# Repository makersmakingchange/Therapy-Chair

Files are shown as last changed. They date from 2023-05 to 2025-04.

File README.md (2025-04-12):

# Therapy Chair
ATP's, PT's, and OT's working with children with physical disabilities often need an appropriate seating system to provide support to enable the kiddo to engage with their environment and participate in strengthening exercises. In the past we measured each child and built it, usually out of triwall, to their size to ensure a good fit. The benefit of this new design is the chair is more durable/easier to clean than triwall and is adjustable. It resembles Swiss cheese to allow placement of laterals virtually anywhere. It can work as a chair or floor sitter. It can incline forward 5 degrees or lay all the way back flat. At the time we are writing this, the cost came in around $100/chair for 7 chairs that we made. This isn't going to work for every kiddo, but we leave it up to you to adapt it further for your unique situation.

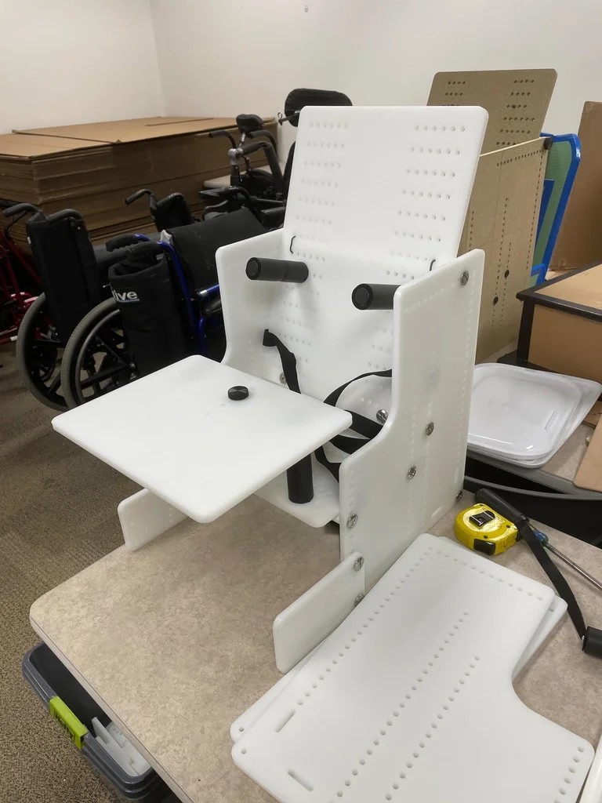
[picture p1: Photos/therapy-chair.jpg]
Picture of Therapy Chair.


<!--
## More info at
- [Makers Making Change Project Page](https://makersmakingchange.com/project/therapy-chair/)
-->

## How to Obtain a Therapy Chair
### 1. Do it Yourself (DIY) or Do it Together (DIT)

This is an open-source assistive technology, so anyone is free to build it. All of the files and instructions required to build the Therapy Chair are contained within this repository. Refer to the Maker Checklist below.

<!--
### 2. Request a build of this device

If you would like to obtain a Therapy Chair, you may submit a build request through the [MMC Library Page](https://makersmakingchange.com/project/therapy-chair/). The requestor is responsible for the cost of materials and any shipping.

### 3. How to build this device for someone else

If you have the skills and equipment to build this device, and would like to donate your time to create the switch for someone who needs it, visit the [MMC Maker Wanted](https://makersmakingchange.com/maker-wanted/) section.
-->

## Getting Started

### 1. Read the Makers Checklist

[The Makers Checklist](/Documentation/Therapy_Chair_Maker_Checklist_V1.0.pdf)

### 2. Order the Off-The-Shelf Components

The [Bill of Materials](/Documentation/Therapy_Chair_BOM_V1.0.xlsx) lists all of the parts and components required to build the Therapy Chair. The main switch component needs to be ordered online. The rest of the off-the-shelf components are also online or may be available in smaller quantities at your local hardware store or dollar store.

### 3. CNC Rout the body panels

The DXF files can be in the [CNC Files](/Build_Files/CNC_Files) folder.

### 4. Assemble the Therapy Chair

Reference the [Assembly Guide](/Documentation/Device-Name_Assembly_Guide_V1.0.pdf) for the tools and steps required to build each portion.

## Files
### Documentation
| Document             | Version | Link |
|----------------------|---------|------|
| Design Rationale     | 1.0     | [Therapy_Chair_Design_Rationale](/Documentation/Therapy_Chair_Design_Rationale_V1.0.pdf)     |
| Maker Checklist      | 1.0     | [Therapy_Chair_Maker_Checklist](/Documentation/Therapy_Chair_Maker_Checklist_V1.0.pdf)     |
| Bill of Materials    | 1.0     | [Therapy_Chair_Bill_of_Materials](/Documentation/Therapy_Chair_BOM_V1.0.xlsx)     |
| Assembly Guide       | 1.0     | [Therapy_Chair_Assembly_Guide](/Documentation/Therapy_Chair_Assembly_Guide_V1.0.pdf)     |
| User Guide           | 1.0     | [Therapy_Chair_User_Guide](/Documentation/Therapy_Chair_User_Guide_V1.0.pdf)    |
| Changelog            | 1.0     | [Therapy_Chair_Changelog](/Documentation/Therapy_Chair_Changelog_V1.0.pdf)     |

### Build Files
 - [CNC Files](/Build_Files/CNC_Files)

## Attribution
Designers:
 - [Design](https://www.instructables.com/Child-Therapy-Chair/) by [Utah Assistive Technology Program](https://www.instructables.com/member/uatpat/)
 - Documentation by Neil Squire Society/Makers Making Change

## License
Everything needed or used to design, make, test, or prepare the Therapy Chair is licensed under the [Attribution-NonCommercial-ShareAlike 4.0 ](https://creativecommons.org/licenses/by-nc-sa/4.0/).

Accompanying material such as instruction manuals, videos, and other copyrightable works that are useful but not necessary to design, make, test, or prepare the THerapy Chair are published under a Creative Commons Attribution-ShareAlike 4.0 license https://creativecommons.org/licenses/by-sa/4.0/ (CC BY-SA 4.0).

----

<!-- ABOUT MMC START -->
## About Makers Making Change
[Makers Making Change Logo](https://www.makersmakingchange.com/)

Makers Making Change is a program of [Neil Squire](https://www.neilsquire.ca/), a Canadian non-profit that uses technology, knowledge, and passion to empower people with disabilities.

Makers Making Change leverages the capacity of community based Makers, Disability Professionals and Volunteers to develop and deliver affordable Open Source Assistive Technologies.

 - Website: [www.MakersMakingChange.com](https://www.makersmakingchange.com/)
 - GitHub: [makersmakingchange](https://github.com/makersmakingchange)
 - Bluesky: [@makersmakingchange.bsky.social](https://bsky.app/profile/makersmakingchange.bsky.social)
 - Instagram: [@makersmakingchange](https://www.instagram.com/makersmakingchange)
 - Facebook: [makersmakechange](https://www.facebook.com/makersmakechange)
 - LinkedIn: [Neil Squire Society](https://www.linkedin.com/company/neil-squire-society/)
 - Thingiverse: [makersmakingchange](https://www.thingiverse.com/makersmakingchange/about)
 - Printables: [MakersMakingChange](https://www.printables.com/@MakersMakingChange)

### Contact Us
For technical questions, to get involved, or to share your experience we encourage you to [visit our website](https://www.makersmakingchange.com/) or [contact us](https://www.makersmakingchange.com/s/contact).
<!-- ABOUT MMC END -->

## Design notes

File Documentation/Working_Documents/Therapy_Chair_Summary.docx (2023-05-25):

# Title

Therapy Chair

## Subtitle

An adjustable therapy chair that is durable and easy to clean.

## Device Details

### Overview

ATP's, PT's, and OT's working with children with physical disabilities often need an appropriate seating system to provide support to enable the kiddo to engage with their environment and participate in strengthening exercises. In the past we measured each child and built it, usually out of triwall, to their size to ensure a good fit. The benefit of this new design is the chair is more durable/easier to clean than triwall and is adjustable. It resembles Swiss cheese to allow placement of laterals virtually anywhere. It can work as a chair or floor sitter. It can incline forward 5 degrees or lay all the way back flat. At the time we are writing this, the cost came in around $100/chair for 7 chairs that we made. This isn't going to work for every kiddo, but we leave it up to you to adapt it further for your unique situation.

### Usage

The overall height from floor to seat bottom can be adjusted by moving the seat bottom and seat back up and down.

The seat depth can be adjusted by repositioning where the hinge pipe bolts onto the seat base.

The seat back angle can be adjusted by moving the support pipe near the top of the seat back forward or back.

The seat base angle can be adjusted by moving the pipe near the front up or down.

Any of the laterals can be repositioned by unscrewing and bolting in a new hole.

The anti-tipper/foot mount has an arc of holes in it. If the child is put into a reclined position and their feet need something to sit on, you can raise and rotate the anti-tipper/foot mount to the appropriate position. From there, you will need to add on your own support, whether you use more sheet plastic or more pieces of PVC pipe to go between the foot mounts.

If the child needs a 5-point harness instead of a chest belt and lap belt, we have one listed on the parts list that was inexpensive. Wrap the straps around the seat back and secure the straps to whatever is appropriate (lateral bolt, PVC pipe, etc.)

### Cost

~$100 per chair

### Build Instructions

This build is mostly using hand tools, but with a small amount of CNC router use to make the body panels.

#### Skills Required

- CNC Routing
- Mechanical Assembly

#### Time Required

Assembly time: 1h

#### Tools

- CNC Router
- Hammer
- Screwdriver
- Scissors
- Tape Measure
- Saw

### Attribution

- Design (https://www.instructables.com/Child-Therapy-Chair/) by the Utah Assistive Technology Program (https://www.instructables.com/member/uatpat/)
- Documentation by Neil Squire Society/Makers Making Change

© 2023 by Neil Squire. This work is licensed under the CC BY SA 4.0 License: http://creativecommons.org/licenses/by-sa/4.0 Files available at https://makersmakingchange.com/project/therapy-chair/ Page 1 of 1

V1.0 | March 2023 Therapy Chair Summary

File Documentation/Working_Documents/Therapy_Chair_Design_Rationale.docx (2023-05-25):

# Introduction

ATP's, PT's, and OT's working with children with physical disabilities often need an appropriate seating system to provide support to enable the kiddo to engage with their environment and participate in strengthening exercises. In the past each child was measured, and a chair built, usually out of Tri-Wall, to their size to ensure a good fit. A customizable therapy chair that can be adjusted in minutes, rather than built in days, would be a helpful tool to have.

# Research

After research, it was found that therapy chairs are commonly custom built to the measurements of each child. This requires the therapist to take measurements and design a custom chair for each new patient. There is a distinct lack of any ready made, adjustable chairs that can accommodate patients of various sizes.

# Requirements

## Goals

G01 | Create an adjustable therapy chair that is durable and easy to clean.

## Functional Requirements

F01 | Chair must be easy to adjust to the child
F02 | Chair must be durable
F03 | Chair must be able to hold the child securely

## Non-functional Requirement

NF01 | Chair must be easy to build
NF02 | Chair must be easy to clean
NF03 | Chair must not have sharp edges or be able to injure the child

## Constraints

C01 | Chair must be made of commonly available parts

# Opportunities for Improvement

Side panels could be updated so that they can be manufactured without the use of a CNC router

© 2023 by Neil Squire. This work is licensed under the CC BY SA 4.0 License: http://creativecommons.org/licenses/by-sa/4.0 Files available at https://makersmakingchange.com/project/therapy-chair/ Page 1 of 1

V1.0 | March 2023 Therapy Chair Design Rationale

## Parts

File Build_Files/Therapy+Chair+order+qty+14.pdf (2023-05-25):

Description | Order qty Total Cost
Charlotte Pipe 1/2‐in dia‐Degree 600 Psi Schedule 40 White PVC Pipe | 14 | 78.54 $ | https://www.lowes.com/pd/Charlotte‐Pipe‐1
S67‐244 3/4in Round | 1/4‐20 Thread Heavy Duty Double Star Metal Tube
Connector $0.48 ea. + $24.00 frieght (Pipe‐12, Laterals 6, Abductor 2) | 280 | 134.40 $

https://www.outwater.com/products/34in‐ro

Frieght S67‐244 3/4in Round | 1/4‐20 Thread | $ | 33.60
Hillman 831490 Stainless Steel Hurricane Bolts (1/4" x 1") ‐ 100 pieces (Pipe‐
16, Laterals 6, Abductor 1) | 3 | 84.57 $ | https://smile.amazon.com/dp/B00MEWLNAS
40Pcs Anwenk 1/4"‐20 x 20mm Furniture Screw in Nut Threaded Wood
Inserts Bolt Fastener Connector Hex Socket Drive for Wood Furniture
Assortment (with Hex Spanner) | 2 | 19.98 $

https://smile.amazon.com/Anwenk‐Furniture

Twenty (20) 1/4‐20 x 1" Long Length Knurled Plastic Head Thumb Screws ‐
Made in USA | 1 | 13.99 $ | https://smile.amazon.com/Twenty‐Length‐Kn
uxcell Foam Tubing for Handle Grip Support, Pipe Insulation, 20mm ID 30mm
OD 1m Length Black 39.37" (39/4"= 9.75) 7 ‐ 4" pieces | 12 | 155.88 $ | https://smile.amazon.com/uxcell‐Tubing‐Han

3/4 Inch Round Plastic Plug / 100 Pack / Black Tubing End Cap Plug / Used
with 14‐20 Gauge Tube Wall Thickness/Durable Chair Glide / Provides
Protection on Flooring (100) by EZENDS. | 1 | 29.81 $

https://smile.amazon.com/Plastic‐Thickness‐P

5 Point Harness Seat Belt Safety Harness Full Protection 5 Point Security
Harness Seatbelt for High Chair and Pushchair Black | 4 | 34.36 $ | https://smile.amazon.com/Harness‐Protectio
Saisn Reusable Fastening Tape Cable Ties 3/4 Inch Double Side Hook Roll (5
Yard, Black)5x3=15, 5.99/15=$0.40 ea. Set | 1 | 5.99 $ | https://smile.amazon.com/dp/B06Y2S7GKT/r

PQPB Garden Twist Ties Soft Reusable Rubber Wire Green Heavy Duty Plant
Support Twine for Gardening,Office,Home (2PCS X 32.8feet, Total
65.8feet),Green ,Rubber Plant Ties Green 65.6ft(PQ10) | 1 | 11.89 $ | https://smile.amazon.com/PQPB‐Reusable‐Ga
3/8 x 4 x 10 White HDPE Panel 80lbs/6 units=16lbs | 2 | 556.00 $
Labor to CNC | 2 | 200.00 $
Total Cost | | $ 1,359.01
Cost Each Chair | $ | 97.07

‐2‐in‐dia‐x‐10‐ft‐L‐600‐PSI‐PVC‐Pipe/3133079

ound‐14‐20‐thread‐heat‐treated‐carbon‐steel‐heavy‐duty‐double‐star‐metal‐tube‐connector/

/ref=twister_B082XW6FR6?_encoding=UTF8&psc=1

e‐Threaded‐Connector‐Assortment/dp/B07VLLKX32/ref=pd_bxgy_img_1/147‐7973450‐5835460?pd_rd_w=FJck7&pf_rd_p=6b3eefea‐7b16‐43e9‐bc45

nurled‐Plastic‐Screws/dp/B01N01IP6M/ref=sr_1_7?keywords=1%2F4‐20+x+1%22+Length+Knurled+Plastic+Head+Thumb+Screws&qid=1647979212&

dle‐Support‐Insulation/dp/B09521L1W2/ref=sr_1_2?crid=1XRFDUEZB6XI2&keywords=20mm%2Bfoam%2Btubing%2Bfor%2Bhandle%2Bgrip%2Bsupp

Provides‐Protection‐Flooring/dp/B07WDRKKZQ/ref=sr_1_9?crid=K1SKVJKQ03T0&keywords=round%2Bplastic%2Bplug%2B20mm%2F0.78&qid=16499

n‐Security‐Seatbelt‐Pushchair/dp/B08ZSHKCK6/ref=pb_allspark_dp_sims_pao_desktop_session_based_2/147‐7973450‐5835460?pd_rd_w=JR3A5&p

ref=twister_B06ZZ59XPX?_encoding=UTF8&psc=1

ardening‐32‐8feet‐65‐8feet/dp/B09H3Y5WB8/ref=sr_1_2_sspa?keywords=Rubber+Twist+Ties&qid=1648191290&sr=8‐2‐spons&psc=1&spLa=ZW5jcn

5‐2e332cbf99da&pf_rd_r=SWXYF3PATKNXXEZH9SE8&pd_rd_r=2325c0df‐c91a‐446d‐a659‐9110172d9653&pd_rd_wg=WTmdd&pd_rd_i=B07HR63VF

s=hi&sr=1‐7

port&qid=1646425796&s=hi&sprefix=20%2Bmm%2Bfoam%2Btubing%2Bfor%2Bhandle%2Bgrip%2Bsupport%2Ctools%2C153&sr=1‐2&th=1

968032&sprefix=round%2Bplastic%2Bplug%2B20%2Bmm%2F0.78%2Caps%2C103&sr=8‐9&th=1

pf_rd_p=e896123b‐6614‐49c5‐873e‐d532e726c2f0&pf_rd_r=R1QVC1M5B8A140S18FSR&pd_rd_r=7d37e6eb‐9433‐4b06‐b6bb‐f519dcca4df7&pd_rd_

nlwdGVkUXVhbGlmaWVyPUEyNEdURDNPRkY4QjU3JmVuY3J5cHRlZElkPUEwNTAzMzkzM0hWV1o2QlVHMlpGTSZlbmNyeXB0ZWRBZElkPUEwMjc4MzY

F5&th=1

_wg=nrkUs&pd_rd_i=B08ZSHKCK6&psc=1

YzMkZPOUlKMlMyR0pJNiZ3aWRnZXROYW1lPXNwX2F0ZiZhY3Rpb249Y2xpY2tSZWRpcmVjdCZkb05vdExvZ0NsaWNrPXRydWU=

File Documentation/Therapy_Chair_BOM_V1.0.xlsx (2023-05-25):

Device: Therapy Chair |  | Total Cost | Total Print time (hr) | Total filament (g)
Version: V1.0 | Date Created: 3/13/2023 | $169.64 | 0.00 | 0
Commercial Parts:
Part type (Electrical. Mechanical, Sanitization, ect) | Part Name | Quantity Needed | Pkg Quantity | Price per package | Price per Unit | Price for qty needed |  | Link
Mechanical | 1/2‐in dia‐Degree 600 Psi Schedule 40 White PVC Pipe | 8 | 10 | $4.71 | $0.47 | $3.77 |  | https://www.homedepot.com/p/JM-EAGLE-1-2-in-x-10-ft-600-PSI-White-Schedule-40-PVC-Pressure-Plain-End-Pipe-530048/100113200
Mechanical | Heavy Duty Double Star Metal Tube Connector | 20 | 1 | $1.25 | $1.25 | $25.00 |  | https://www.outwater.com/S67-PARENT?quantity=1&purchase-option=11&tube-size=1
Mechanical | Sidewalk Bolt 1/4 x 1 | 20 | 100 | $32.99 | $0.33 | $6.60 |  | Hillman Group Combo Sidewalk Bolt, Hurricane Hardware, 100 Pieces, Rust-Resistant, Durable, Truss Head, (1/4" x 1") Stainless Steel Finish (831490) (amazon.com) (https://www.amazon.com/dp/B00MEWLNAS?redirectFromSmile=1)
Mechanical | Anwenk 1/4"-20 x 20mm Furniture Screw | 1 | 40 | 18.45 | $0.46 | $0.46 |  | https://www.amazon.ca/Anwenk-Furniture-Threaded-Connector-Assortment/dp/B07VLLKX32?th=1
Mechanical | 1/4-20 x 1-1/2" Long Length Knurled Plastic Head Thumb Screws | 1 | 20 | 26.63 | $1.33 | $1.33 |  | https://www.amazon.ca/Twenty-Length-Knurled-Plastic-Screws/dp/B075VJKBLS
Mechanical | Foam Tubing for Handle Grip Support | 0.5 | 1 | 16.92 | $16.92 | $8.46 |  | Foam Grip Tubing Handle Grips Pipe Insulation,20mm ID 30mm OD 1m Length,Non-Slip for Fitness,Tools Handle Support,Black : Amazon.ca: Tools & Home Improvement (https://www.amazon.ca/Tubing-Insulation-Non-Slip-Fitness-Support/dp/B0BB278FRJ?s=hi)
Mechanical | Black Tubing End Cap Plug | 4 | 20 | 12.98 | $0.65 | $2.60 |  | https://www.amazon.ca/Round-Plastic-Tubing-Furniture-Insert/dp/B098QRJTBH
Mechanical | 5 Point Harness Seat Belt | 1 | 1 | 9.99 | $9.99 | $9.99 |  | https://www.amazon.com/Harness-Protection-Security-Seatbelt-Pushchair/dp/B08ZSHKCK6
Mechanical | Saisn Reusable Fastening Tape | 0.1 | 1 | 6.99 | $6.99 | $0.70 |  | Saisn Reusable Fastening Tape Cable Ties 3/4 Inch Double Side Hook Roll (5 Yard, Black) (amazon.com) (https://www.amazon.com/dp/B06Y2S7GKT/r?redirectFromSmile=1)
Mechanical | Heavy Duty Plant Support Twine | 0.05 | 1 | 11.98 | $11.98 | $0.60 |  | https://www.amazon.com/PQPB-Reusable-Gardening-32-8feet-65-8feet/dp/B09H3Y5WB8
Mechanical | 3/8" x 48" x 96" HDPE Sheet | 0.4 | 1 | 275.35 | $275.35 | $110.14 | Plywood can be used here | https://www.usplastic.com/catalog/item.aspx?itemid=41935
3D Printed Parts ESTIMATED PRICING USING 1KG ROLL COST: | $25.00
Part | Description | Quantity Needed | TOTAL Mass (g) | Estimated Price | Print Time (Min) | Link
See build files for CNC DXF files |  |  |  | $0.00
 |  |  |  | $0.00
 |  |  |  | $0.00
 |  |  |  | $0.00
 |  |  |  | $0.00
 |  |  | Total Print Cost: | $0.00
Tools for Assembly
Alternatives (if there are other sources for some parts link them below)
Part and description | Link
PVC pipe | https://www.amazon.ca/Pipe-Sch40-White-Custom-Length/dp/B09GL4G2MC

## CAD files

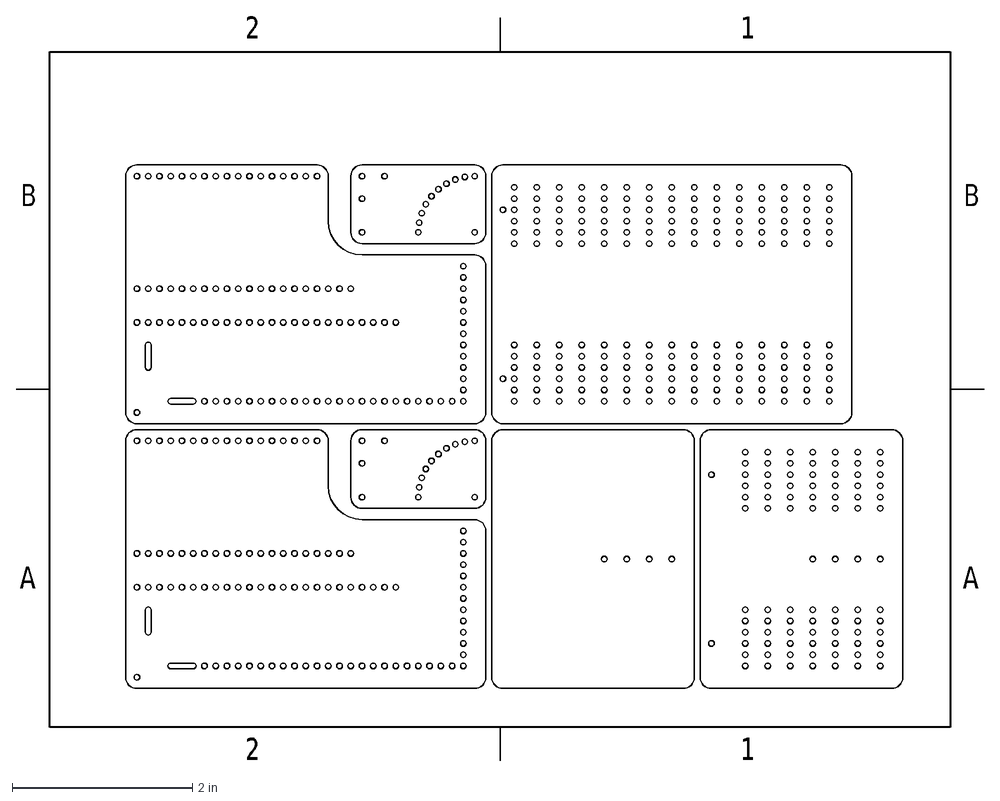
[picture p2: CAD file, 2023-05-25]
Build_Files/CNC_Files/sheet+parts+layout.DXF
A
B
2
1

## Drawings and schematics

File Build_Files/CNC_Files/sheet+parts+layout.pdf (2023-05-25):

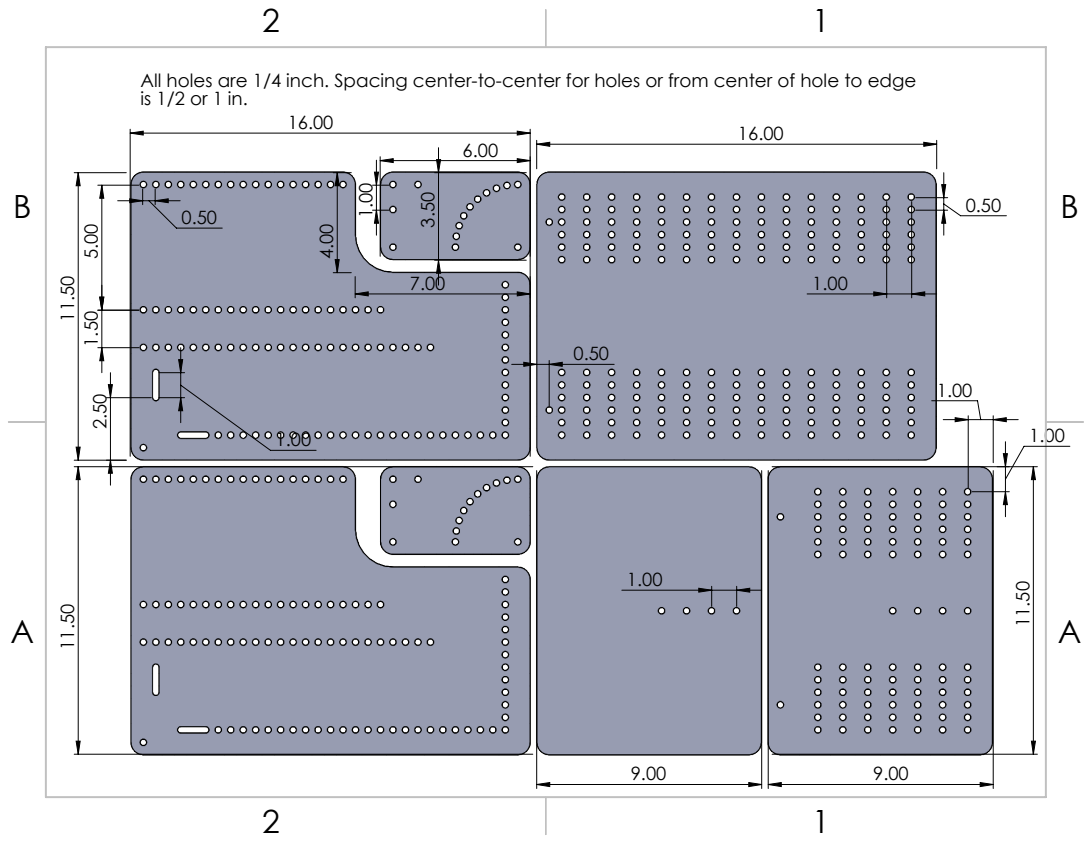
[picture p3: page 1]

All holes are 1/4 inch. Spacing center-to-center for holes or from center of hole to edge

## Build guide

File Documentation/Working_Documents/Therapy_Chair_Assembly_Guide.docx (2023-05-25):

# Required Components

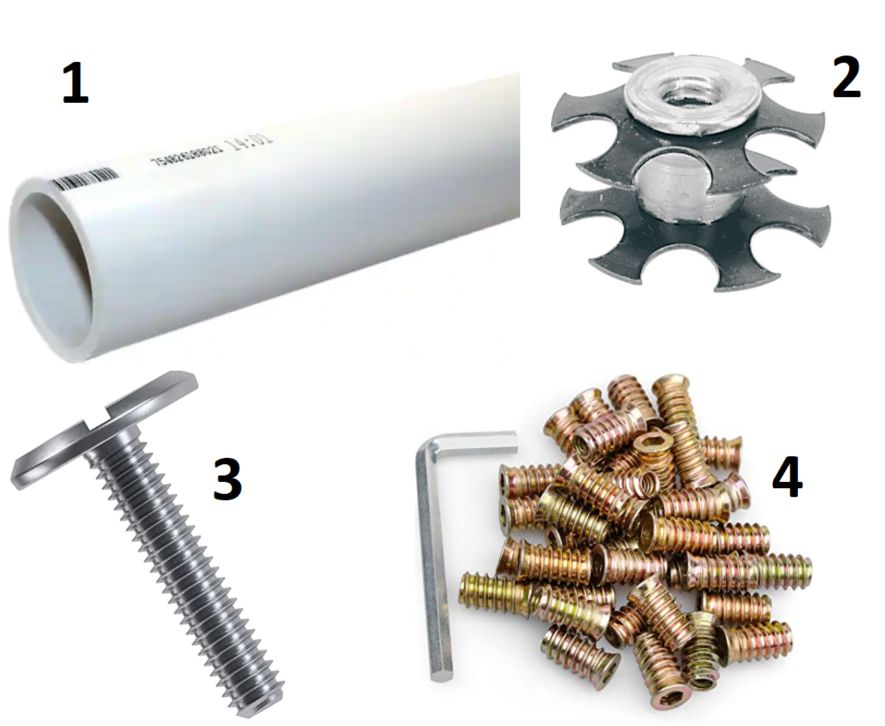
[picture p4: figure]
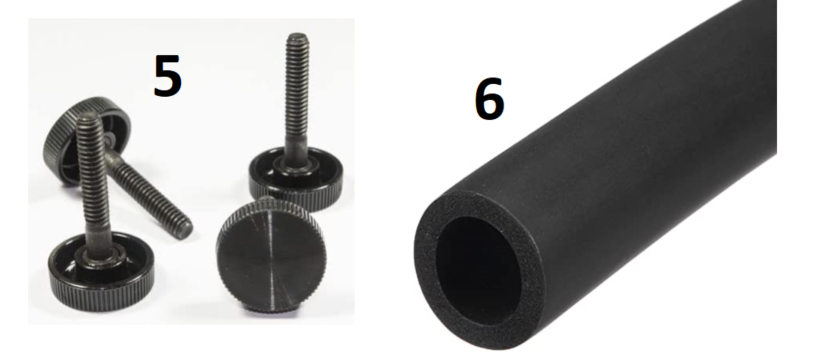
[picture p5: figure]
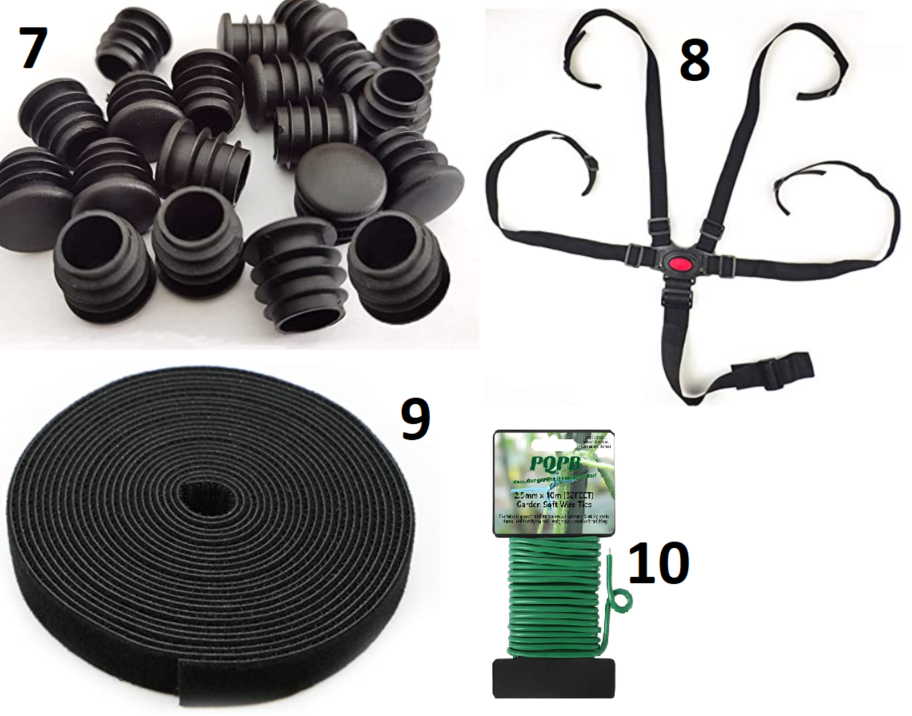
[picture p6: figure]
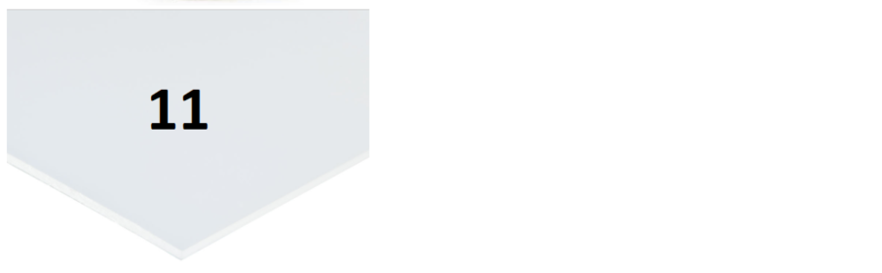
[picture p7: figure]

| BOM 1. ½-in PVC pipex 8ft 2. ¼-20 Pipe Connector x20 3. ¼-20 1 inch hurricane bolts x 20 4. ¼-20 20mm furniture screw inserts x1 5. ¼-20 1-1/2 Thumb screw x1 6. Foam tubing x 50cm 7. Tubing End Cap Plug x4 8. 5 point harness seat belt x1 9. Fastening tape x1 metre 10. Plant support twine x1 metre 11. HDPE Sheet x1

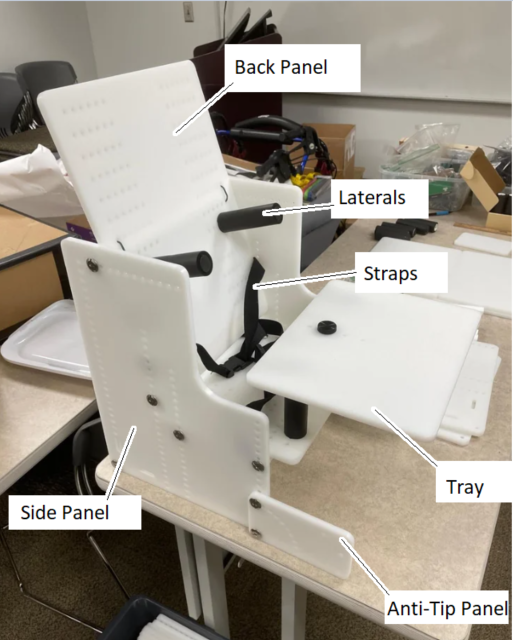
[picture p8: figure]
A photo of the assembled chair sitting on a table, with all the features labeled

# Required Tools

- CNC Router
- Hammer
- Tape measure
- Screwdriver
- Scissors
- Saw
- Sandpaper

# Required Personal Protective Equipment (PPE)

- Eye Protection

# Assembly Instructions

## Step 1

Cut the PVC pipe for the supports. You will need to cut

- 5x 11.5 in piece for the frame
- 6x 3.875 in piece for laterals and head supports
- 1x 4.125 in piece for abdicator.

After cutting, sand off any burrs.

## Step 2

Cut the main body out of the sheet plastic, or plywood if the plastic is hard to source. Use a CNC router and the DXF files provided. The grid of holes in the design are simply there to allow the laterals to be adjustable. A "quick-and-dirty" version could forget all the holes and add them in as the child grows.

## Step 3

Drill two 0.375 inch holes in two of the 11.5 inch pipes, 2 inches from each end. These will become the hinge pipes for the seat base and back. Keeping the holes straight here will save grief later.

## Step 4 (https://www.youtube.com/watch?v=EUsNI3QqX5g)

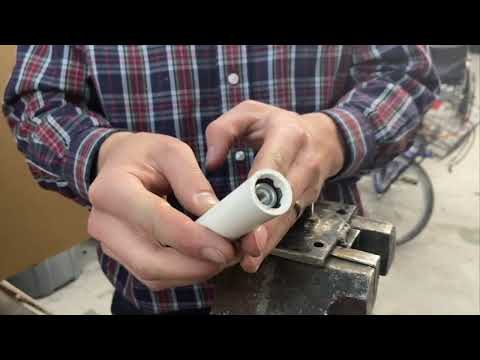
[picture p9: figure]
Child Therapy Chair Part 1: Laterals and Abductors

Pound in the barbed inserts into one end of the 3.875 inch pipes.

Pound in the caps into other end of the 3.875 inch pipes.

Place the foam over the PVC pipe and trim it to cover the pipe entirely, none of the pipe should be showing.

## Step 5

Pound in the barbed inserts into both ends of the 4.125 inch pipe.

Cut foam to length as in step 4. Note in the attached picture, the foam is too short, there should be none of the pipe still showing.

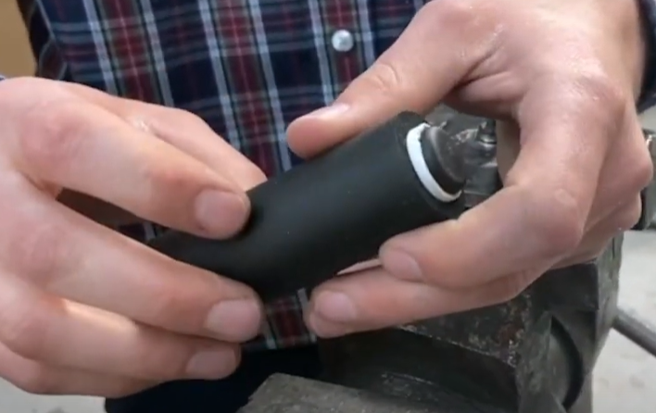
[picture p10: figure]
A photo of an assembled lateral support, with end cap and foam attached

## Step 6

Pound in the barbed inserts into both ends of all the 11.5 inch pipes.

Twist in the thread inserts into the two 11.5 inch hinge pipes.

## Step 7 (https://www.youtube.com/watch?v=JkeG7XiT2Fk)

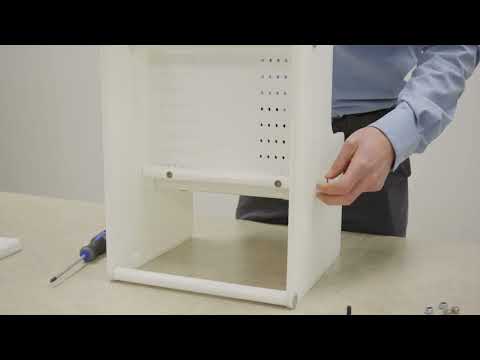
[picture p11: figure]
Child Therapy Chair, Part 2

Following the instructions in the video, Connect the hinge pipe to the seat back and bottom using the bolts.

Connect the two sides together using the other 11.5 inch pipes and bolts. Don't snug tight yet.

## Step 8

Add the seat base and back using more bolts.

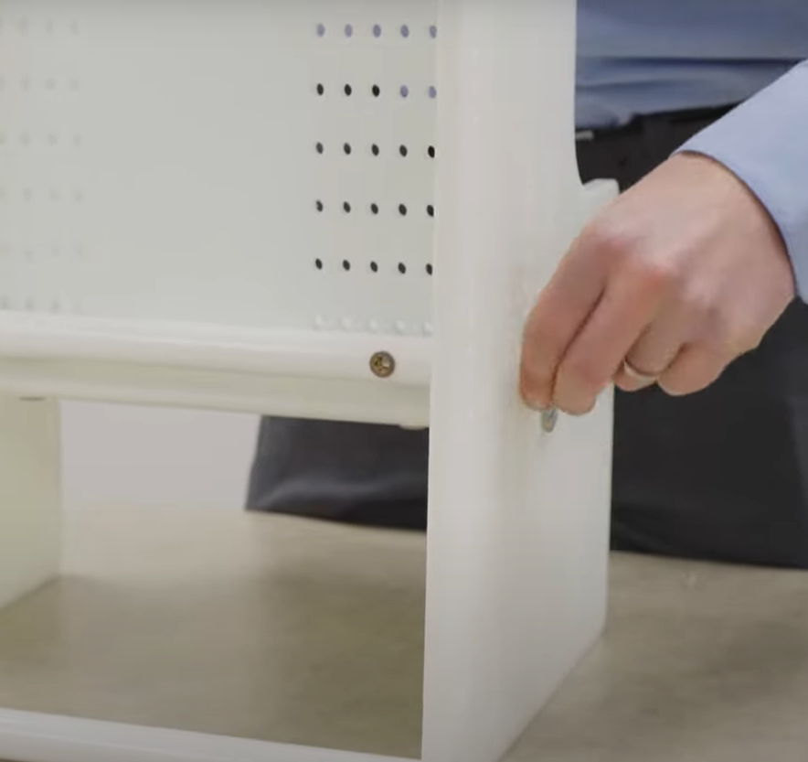
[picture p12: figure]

## Step 9

Add the laterals.

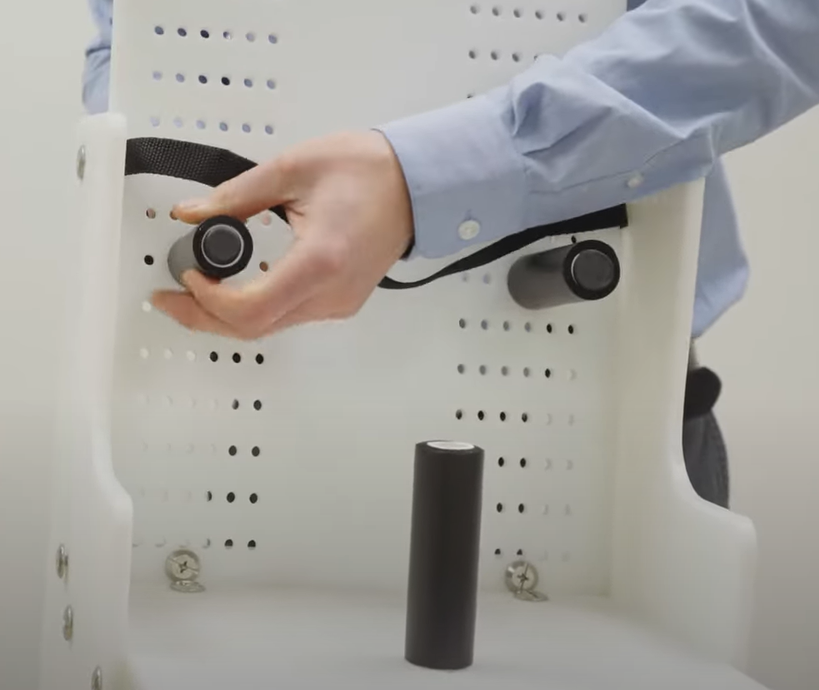
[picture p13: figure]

Loop the seat belt around the seat base and back. Once you have the belt in the correct spot/height, feel free to tighten all the bolts and it will stop the belt from moving around.

If desired, add the anti tipper/foot rest mount onto the front of the chair. (rectangle plastic added on the front)

## Step 10

Use the knob to secure the tray into the abductor.

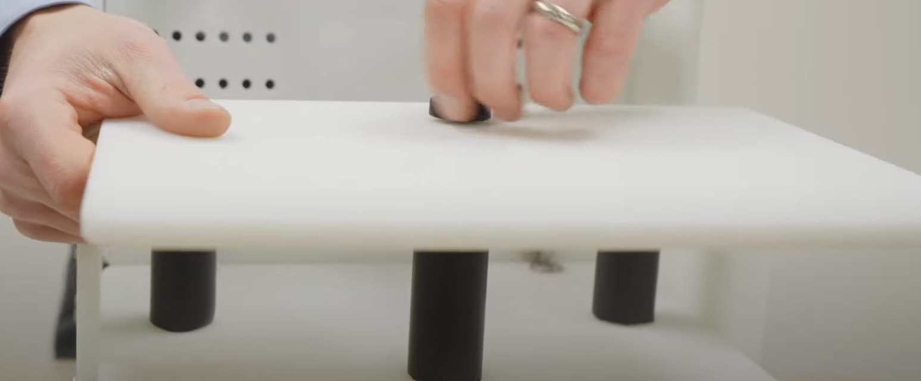
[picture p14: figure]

Add twist ties onto the top of the seat back if needed to stop from rocking forward.

Add straps through the back and bottom of the chair using the slots to secure it to a chair if desired.

## Step 11

The overall height from floor to seat bottom can be adjusted by moving the seat bottom and seat back up and down.

The seat depth can be adjusted by repositioning where the hinge pipe bolts onto the seat base.

The seat back angle can be adjusted by moving the support pipe near the top of the seat back forward or back.

The seat base angle can be adjusted by moving the pipe near the front up or down.

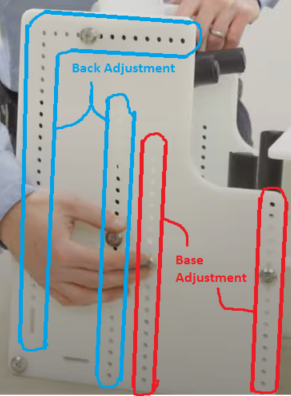
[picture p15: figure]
A picture of the side of the therapy chair, with the base and back adjustment points highlighted.

Any of the laterals can be repositioned by unscrewing and bolting in a new hole.

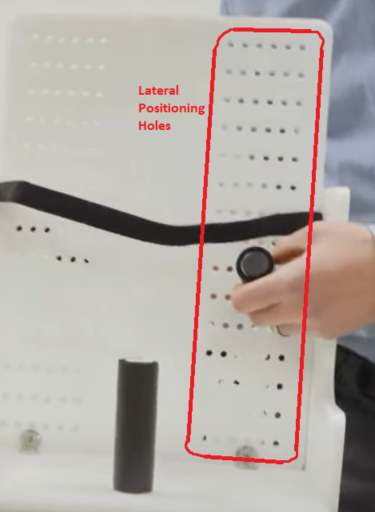
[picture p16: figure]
Photo of the back of the chair with the lateral adjustment points highlighted

The anti-tipper/foot mount has an arc of holes in it. If the child is put into a reclined position and their feet need something to sit on, you can raise and rotate the anti-tipper/foot mount to the appropriate position. From there, you will need to add on your own support, whether you use more sheet plastic or more pieces of PVC pipe to go between the foot mounts.

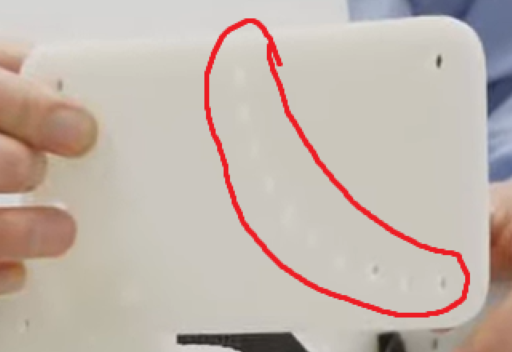
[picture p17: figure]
Photo of the anti-tipper/foot mount with the adjustment points highlighted

If the child needs a 5 point harness instead of a chest belt and lap belt, we have one listed on the parts list that was inexpensive. Wrap the straps around the seat back and secure the straps to whatever is appropriate (lateral bolt, pvc pipe, etc).

© 2023 by Neil Squire. This work is licensed under the CC BY SA 4.0 License: http://creativecommons.org/licenses/by-sa/4.0 Files available at https://makersmakingchange.com/project/therapy-chair/ Page 1 of 1

V1.0 | March 2023 Therapy chair Assembly Guide

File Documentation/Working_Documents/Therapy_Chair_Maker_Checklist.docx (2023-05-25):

# Maker To Do List

- Read through the Assembly Guide to become familiar with required components, tools, supplies, and safety gear and overall assembly steps.
- Talk to User about customization options (e.g., color, any special requests, harness, footrests, etc.)
- Order hardware components
- Gather tools, supplies, and safety equipment.
- Cut the CNC parts
- Assemble the device
- Test device
- Print “User Quick Guide”

# Items to Give to User

- Assembled, tested device
- “User Quick Guide”

© 2023 by Neil Squire. This work is licensed under the CC BY SA 4.0 License: http://creativecommons.org/licenses/by-sa/4.0 Files available at https://makersmakingchange.com/project/therapy-chair/ Page 1 of 1

V1.0| March 2023 Therapy Chair Maker Checklist

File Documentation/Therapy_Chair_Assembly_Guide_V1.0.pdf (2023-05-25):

V1.0 | March 2023

## Therapy chair

## ASSEMBLY GUIDE

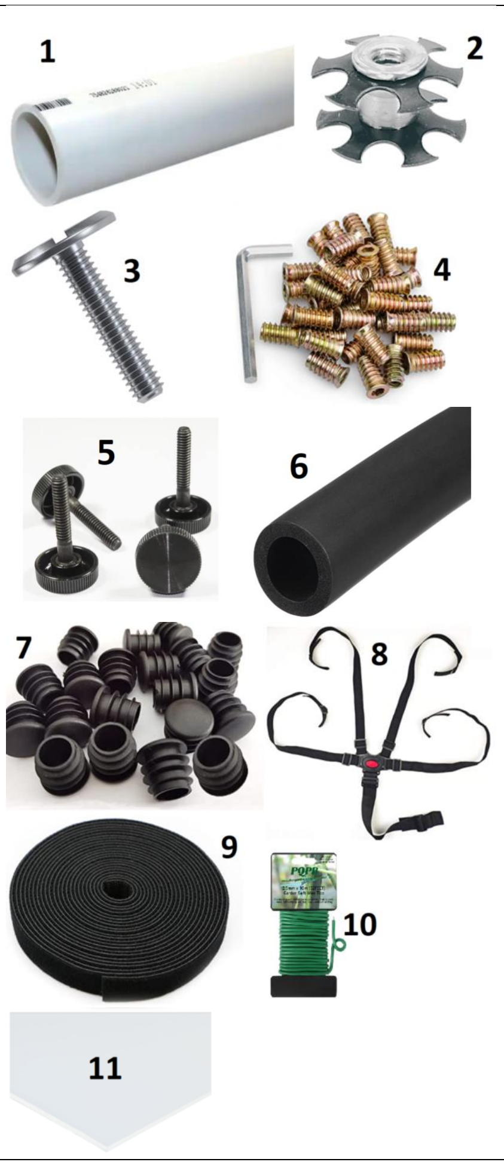
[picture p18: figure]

© 2023 by Neil Squire. (https://neilsquire.ca/)
This work is licensed under the CC BY SA 4.0 License: http://creativecommons.org/licenses/by-sa/4.0
Files available at https://makersmakingchange.com/project/therapy-chair/ | Page 1 of 9

Required Components

BOM
1. ½-in PVC pipex 8ft
2. ¼-20 Pipe Connector x20
3. ¼-20 1 inch hurricane bolts x 20
4. ¼-20 20mm furniture screw inserts x1
5. ¼-20 1-1/2 Thumb screw x1
6. Foam tubing x 50cm
7. Tubing End Cap Plug x4
8. 5 point harness seat belt x1
9. Fastening tape x1 metre
10. Plant support twine x1 metre
11. HDPE Sheet x1

## ASSEMBLY GUIDE

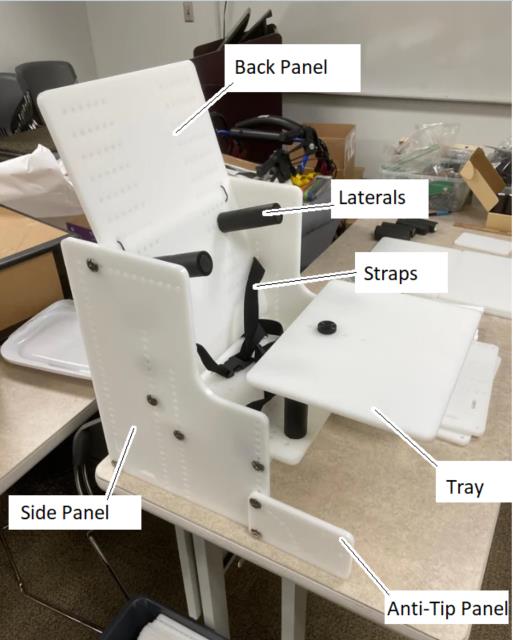
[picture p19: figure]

Files available at https://makersmakingchange.com/project/therapy-chair/ | Page 2 of 9

Required Tools

- CNC Router
- Hammer
- Tape measure
- Screwdriver
- Scissors
- Saw
- Sandpaper

Required Personal Protective Equipment (PPE)

- Eye Protection

Assembly Instructions

Step 1
Cut the PVC pipe for the supports. You will need to cut
- 5x 11.5 in piece for the frame
- 6x 3.875 in piece for laterals and head supports

## ASSEMBLY GUIDE

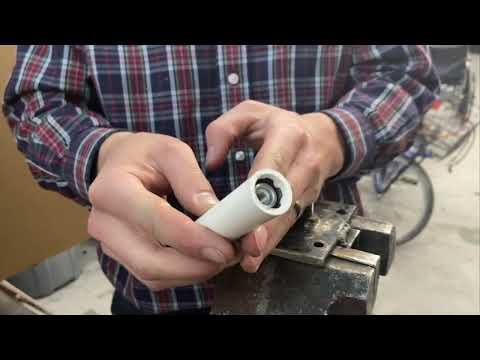
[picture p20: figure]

Files available at https://makersmakingchange.com/project/therapy-chair/ | Page 3 of 9
- 1x 4.125 in piece for abdicator.

After cutting, sand off any burrs.

Step 2
Cut the main body out of the sheet plastic, or plywood if the plastic is hard to source. Use a CNC router and the DXF files provided. The grid of holes in the design are simply there to allow the laterals to be adjustable. A "quick-and-dirty" version could forget all the holes and add them in as the child grows.
Step 3
Drill two 0.375 inch holes in two of the 11.5 inch pipes, 2 inches from each end. These will become the hinge pipes for the seat base and back. Keeping the holes straight here will save grief later.
Step 4 (https://www.youtube.com/watch?v=EUsNI3QqX5g)

Pound in the barbed inserts into one end of the 3.875 inch pipes.

Pound in the caps into other end of the 3.875 inch pipes.

Place the foam over the PVC pipe and trim it to cover the pipe entirely, none of the pipe should be showing.

## ASSEMBLY GUIDE

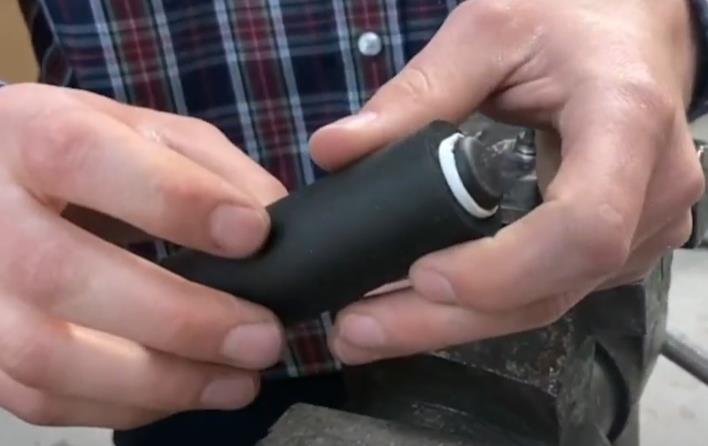
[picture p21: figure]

Files available at https://makersmakingchange.com/project/therapy-chair/ | Page 4 of 9
Step 5
Pound in the barbed inserts into both ends of the 4.125 inch pipe.

Cut foam to length as in step 4. Note in the attached picture, the foam is too short, there should be none of the pipe still showing.

Step 6
Pound in the barbed inserts into both ends of all the 11.5 inch pipes.

Twist in the thread inserts into the two 11.5 inch hinge pipes.

## ASSEMBLY GUIDE

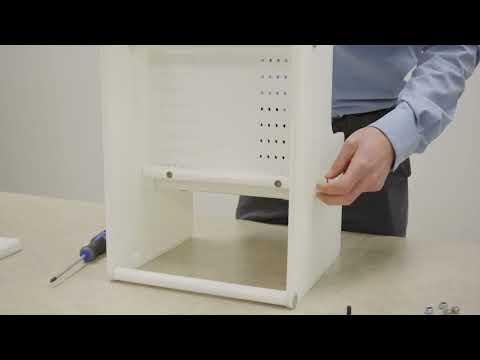
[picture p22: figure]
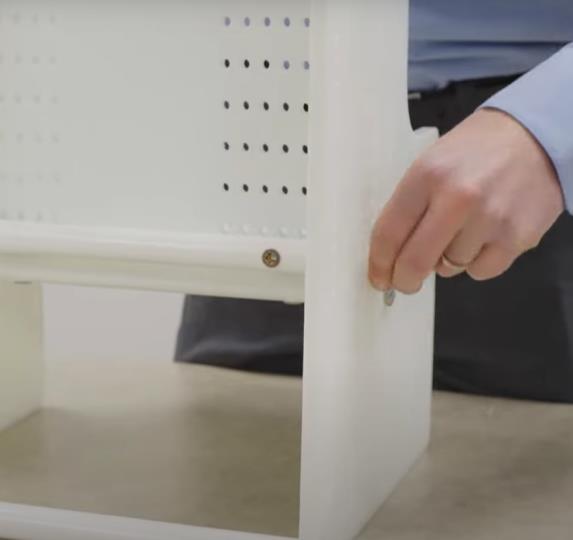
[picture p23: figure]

Files available at https://makersmakingchange.com/project/therapy-chair/ | Page 5 of 9
Step 7 (https://www.youtube.com/watch?v=JkeG7XiT2Fk)

Following the instructions in the video, Connect the hinge pipe to the seat back and bottom using the bolts.

Connect the two sides together using the other 11.5 inch pipes and bolts. Don't snug tight yet.

Step 8
Add the seat base and back using more bolts.

## ASSEMBLY GUIDE

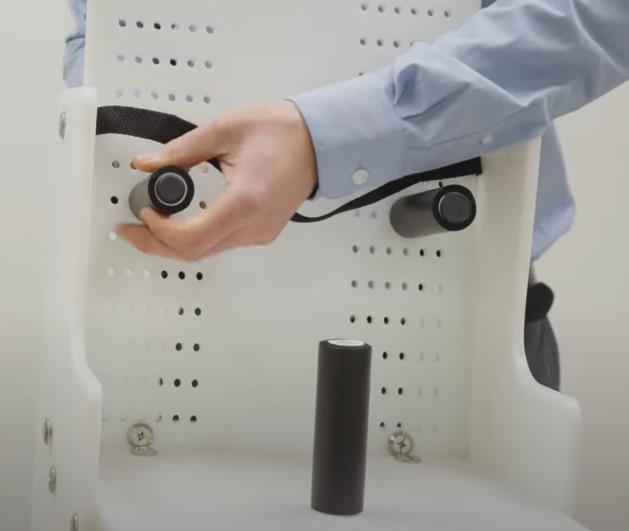
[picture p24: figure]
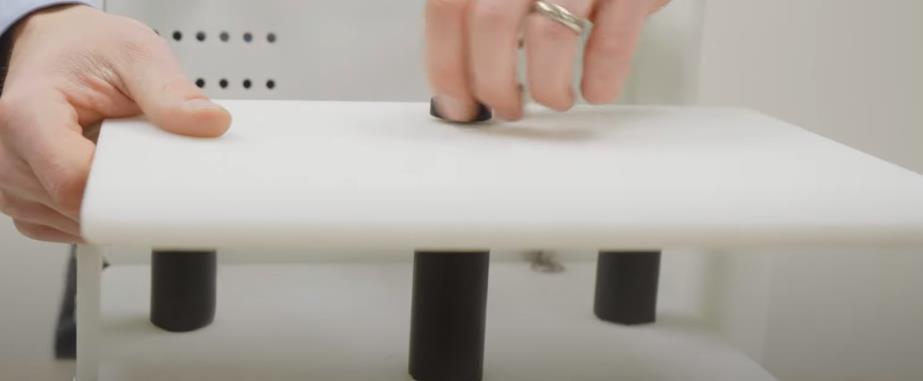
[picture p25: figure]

Files available at https://makersmakingchange.com/project/therapy-chair/ | Page 6 of 9
Step 9
Add the laterals.

Loop the seat belt around the seat base and back. Once you have the belt in the correct spot/height, feel free to tighten all the bolts and it will stop the belt from moving around.

If desired, add the anti tipper/foot rest mount onto the front of the chair. (rectangle plastic added on the front)

Step 10
Use the knob to secure the tray into the abductor.

Add twist ties onto the top of the seat back if needed to stop from rocking forward.

Add straps through the back and bottom of the chair using the slots to secure it to a chair if desired.

## ASSEMBLY GUIDE

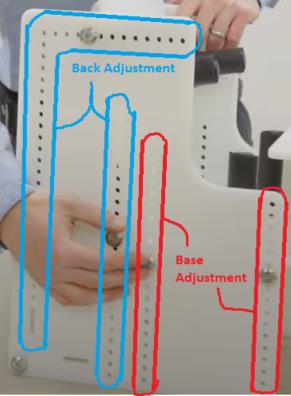
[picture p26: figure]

Files available at https://makersmakingchange.com/project/therapy-chair/ | Page 7 of 9
Step 11
The overall height from floor to seat bottom can be adjusted by moving the seat bottom and seat back up and down.

The seat depth can be adjusted by repositioning where the hinge pipe bolts onto the seat base.

The seat back angle can be adjusted by moving the support pipe near the top of the seat back forward or back.

The seat base angle can be adjusted by moving the pipe near the front up or down.

Any of the laterals can be repositioned by unscrewing and bolting in a new hole.

## ASSEMBLY GUIDE

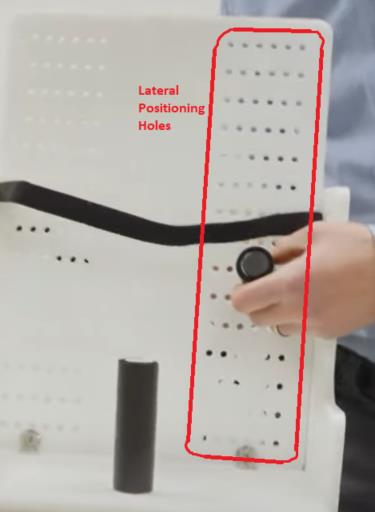
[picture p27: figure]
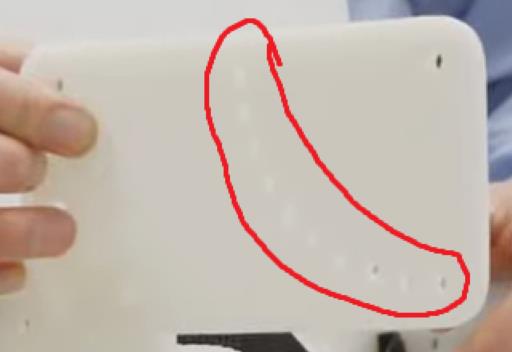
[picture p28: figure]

Files available at https://makersmakingchange.com/project/therapy-chair/ | Page 8 of 9

The anti-tipper/foot mount has an arc of holes in it. If the child is put into a reclined position and their feet need something to sit on, you can raise and rotate the anti-tipper/foot mount to the appropriate position. From there, you will need to add on your own support, whether you use more sheet plastic or more pieces of PVC pipe to go between the foot mounts.

If the child needs a 5 point harness instead of a chest belt and lap belt, we have one listed on the parts list that was inexpensive. Wrap the straps around the seat back and secure the straps to whatever is appropriate (lateral bolt, pvc pipe, etc).

## ASSEMBLY GUIDE

Files available at https://makersmakingchange.com/project/therapy-chair/ | Page 9 of 9
